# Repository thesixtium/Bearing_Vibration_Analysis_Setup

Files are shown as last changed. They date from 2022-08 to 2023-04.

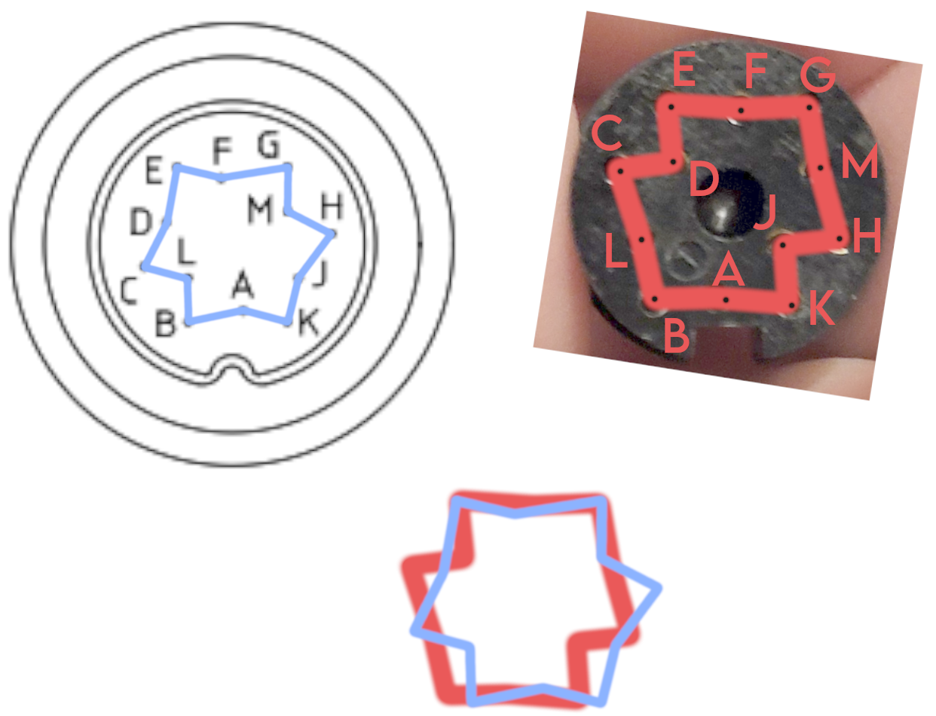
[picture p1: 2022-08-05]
Hole Alignment.png

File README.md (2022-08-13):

## Bearing Vibration Analysis Setup
I worked on the electrical and software design for this project. It is *extremely* loosely based on the setup shown in "A Novel Tribometer Designed
to Evaluate Geological Sliding
Contacts Lubricated by Drilling Muds" in the Journal of Testing and Evaluation, published by Philip Egberts, Nicholas Simin, Calvin Wong, Jan Czibor, Curtis Ewanchuk, and Simon Par.

The goal of this project is to research faults in bearings, and see if specific vibrations can be recorded to predict not only a fault in a bearing ahead of time but also what the fault is caused by.

The two main parts of this project was electrically connecting everything properly, and then coding everything to work. The main electrical parts are:
* NI myDAQ
* AC Motor
* Torque Sensor
* AC Motor PSU
* Torque Sensor PSU

The electrical was mostly just wiring connections between different parts, however, an opamp had to be wired and installed to allow a voltage range expansion on the controlling DAQ.

The software was all done in LabVIEW and was focused on getting the torque sensor to act in a feedback loop with the motor in order to control the motor's speed.

I made good progress on this project, but there was just not enough time to finish it during my summer term.

### Link to GitHub
You can find the project-specific GitHub here:
[thesixtium/Bearing_Vibration_Analysis_Setup](https://github.com/thesixtium/Bearing_Vibration_Analysis_Setup)

### What's Been Done
* The electrical schematics were made according to specifications by the head Ph.D. student. 
* Version 1 of the electrical setup was tested. It didn’t reach the full 42V range because of an oversight in the opamp chip (although rated to go to a full 42V, it only had a gain of 5V). Everything else worked through.
* Version 2 of the electrical was tested. Everything seemed to work, but because the opamp came in a smaller package than expected (TSSOP) and because the protoboard was being soldered by hand, this lead to a short that caused the board to fail.

### What Needs to Happen
* The protoboard that is the current circuit needs to be redone to fix the solder. Instead of ordering more parts and trying to do everything by hand, I would recommend making an actual PCB for it. The protoboard was only tried because it was faster and guaranteed to give me enough time for 2 attempts and was easy to resolder parts if needed. Redo circuit board, probably print an actual PCB
* Range scaling and calibration need to be added to the LabVIEW program to allow for easier control of the motor feedback loop. Currently, the numbers are not mapped to any understandable value and are pretty arbitrary outside of having a mix between a logarithmic and linear relationship with the motor's speed.
* The integration of the accelerometers and brake integration needs to be done, they weren't a priority at the start of this project for electrical so they were largely ignored.

### Documentation
All the needed documentation is on the project's GitHub, with “Bearing Information.pptx” being the most up-to-date and informative file on everything. There is also a bunch of supporting documentation.

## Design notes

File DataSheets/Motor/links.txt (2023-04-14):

http://wentec.com/unipower/calculators/power_torque.asp?print=true
https://www.usarollerchain.com/90-Volt-1-3-HP-DC-Electric-Motor-p/wpmdc13-18-90v-56cb.htm
https://worldwideelectric.com/product/wpmdc14-18-90v-56cb/

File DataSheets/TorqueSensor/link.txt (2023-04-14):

httpswww.kistler.comINTencpshaft-torque-sensors-basic-line-torque-transducers-measuring-ranges-1-to-1000-nm-4520aP0000241

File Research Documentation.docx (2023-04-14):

Research Documentation

# The Parts

## PCB

### PCB Schematics

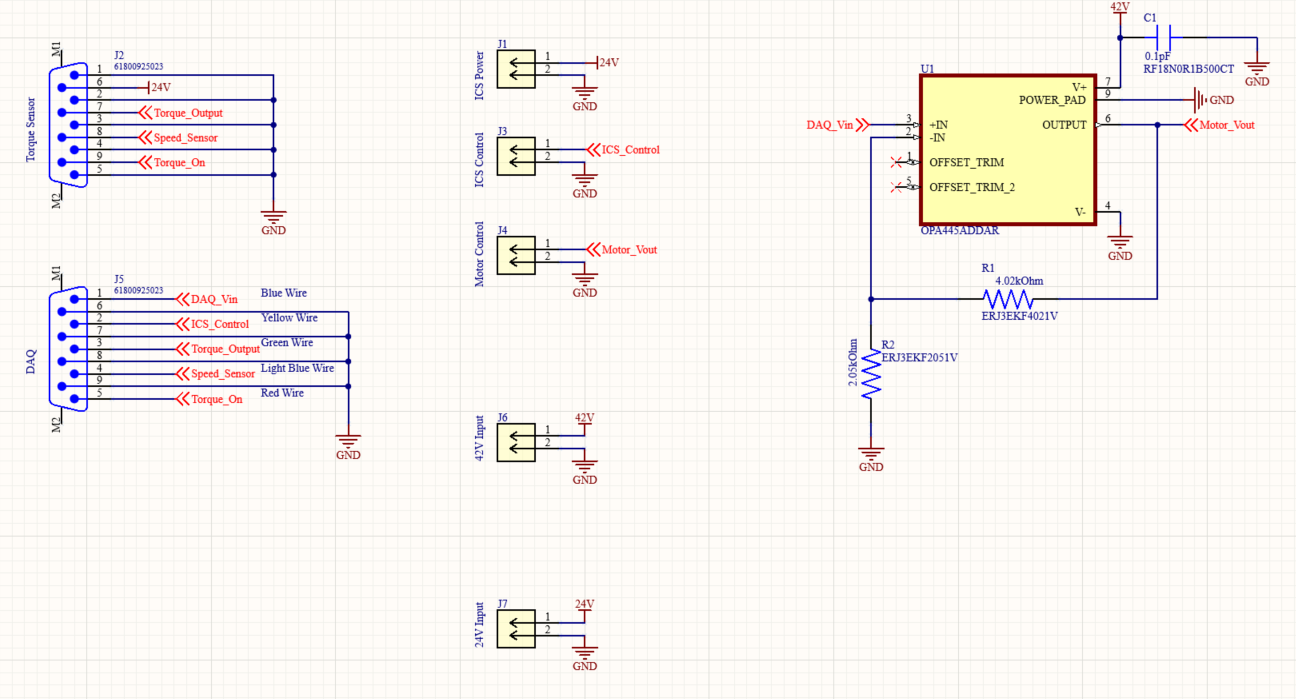
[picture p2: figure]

#### How to read the above schematic

All red and red-adjacent labels are “net labels”; all blue wires connected to the same net label are connected together. For example, everything connected to the “ICS_Control” label is connected together.

The two parts labeled “Torque Sensor” and “DAQ” are db 9 connectors, specifically the “61800925023” connector available on DigiKey at the following link: 61800925023 Würth Elektronik | Connectors, Interconnects | DigiKey (https://www.digikey.com/en/products/detail/w%C3%BCrth-elektronik/61800925023/10484653). They are serial connectors used to connect the torque sensor and the DAQ to other components.

The five yellow squares (each one has two arrows pointing to the left) are BNC connectors, similar in function to the db 9 connectors. They are all labeled to what they connect to, which (top to bottom) is the power for the ICS, the control signals for the ICS, the control signals for the motor, the input connector for the 42 volt supply, and the input connector for the 24 volt supply.

Finally, the circuit on the right is a whole bunch of components connected together to form an amplifier, to change the output from the DAQ from a range of [0v, 15v] to [0v, 42v]. The circuit is a negative feedback operational amplifier circuit. The big yellow box in the middle (labeled on top at U1, and on the bottom as OPA445ADDAR) is an operational amplifier, usually known as an op-amp, and functions to add gain to the voltage. It is configured in a negative feedback loop, which is when you connect the output of an op-amp to its inverting (-) input. It makes a dynamic system where the output signal is “fed back” to the input somehow so as to reach a point of equilibrium, which in this case is an amplification of about 3 times. The two resistors (R1 and R2, represented by zigzag lines) set what the gain of the amplifier will be. The equation for gain is 1+(R2/R1), thus the gain of this circuit is about 1+(4/2) = 3.

< - - - Documentation Stopped As Documentation Is No Longer Needed - - ->

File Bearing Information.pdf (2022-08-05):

# Bearing Testing Rig

## What Aleks has done

# Week 1

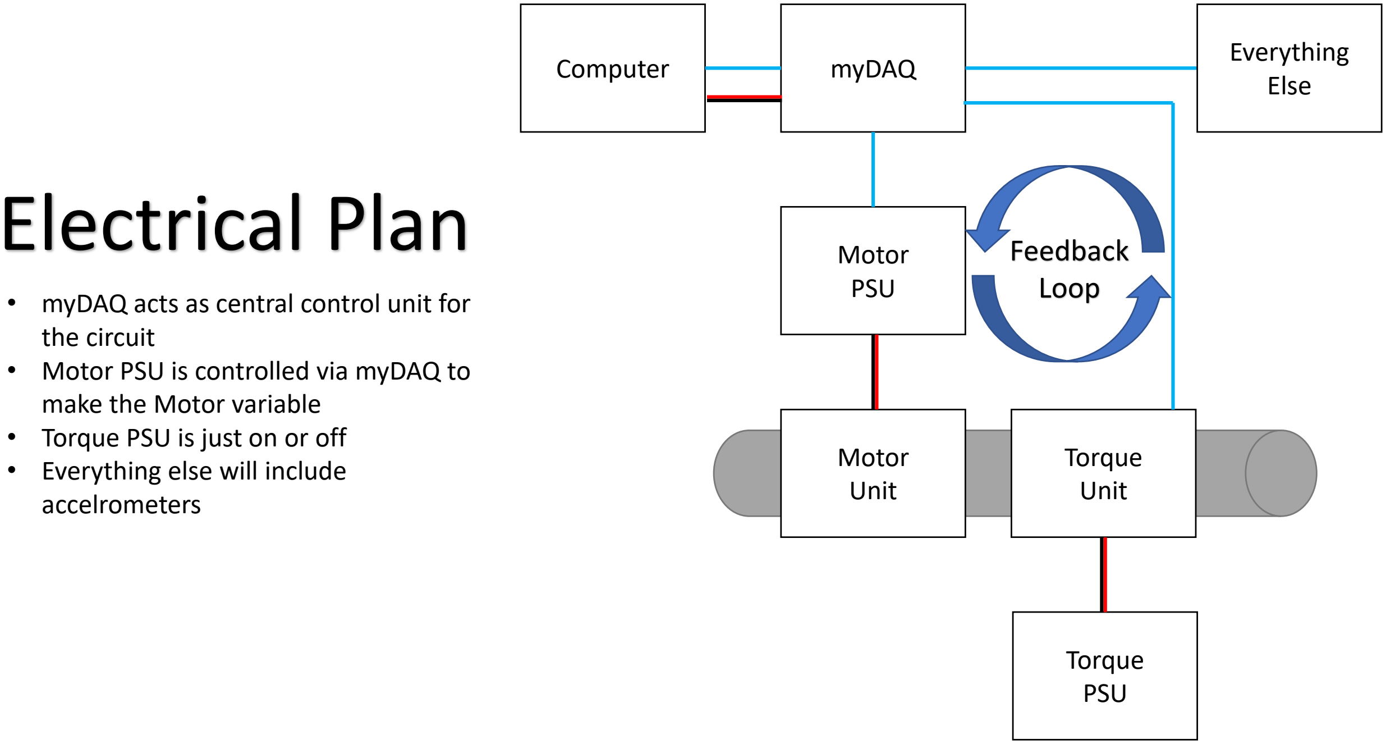
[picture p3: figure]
myDAQ; Motor PSU; Torque PSU; Computer; Torque Unit; Motor Unit; Everything Else; Feedback Loop; Electrical Plan; the circuit • Motor PSU is controlled via myDAQ to make the Motor variable • Torque PSU is just on or off • Everything else will include accelrometers

- myDAQ acts as central control unit for

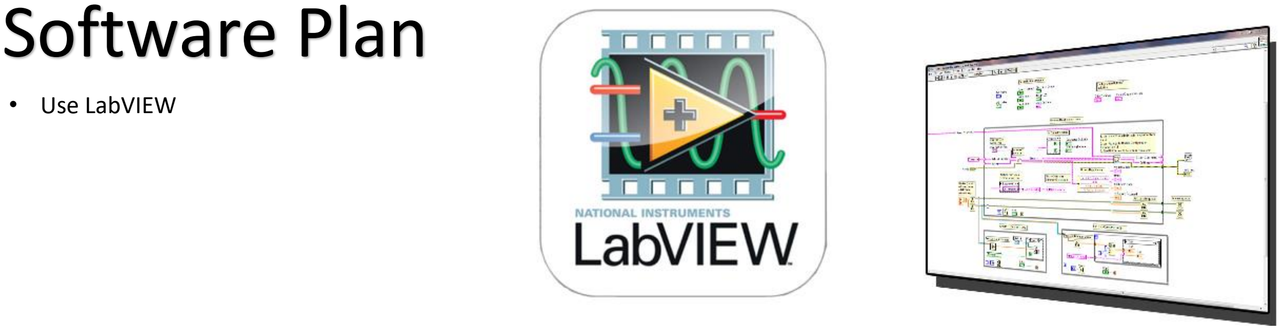
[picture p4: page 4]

# Software Plan

- Use LabVIEW

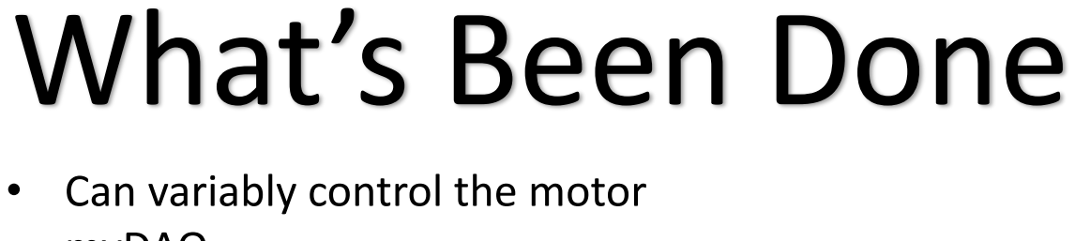
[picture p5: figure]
What’s Been Done; • Can variably control the motor

myDAQ
- Need the cable for the torque sensor to do the rest of it
- Need to know what “Everything Else” entails
- How do we want the data out?

# Week 2

# EM Brake: AHB-5 Air-Cooled Hysteresis Brake

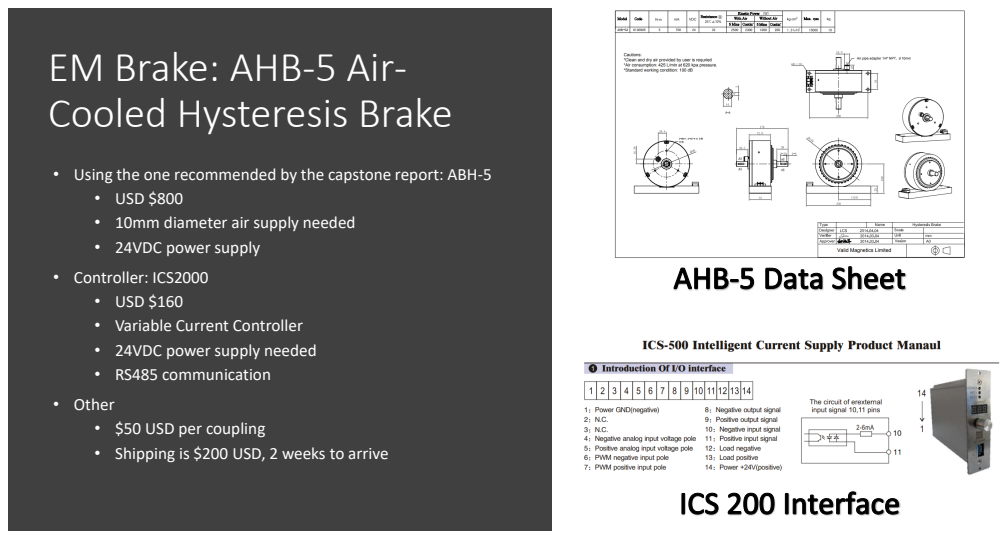
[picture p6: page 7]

• Using the one recommended by the capstone report: ABH-5
• USD $800
• 10mm diameter air supply needed
• 24VDC power supply
• Controller: ICS2000
• USD $160
• Variable Current Controller
• 24VDC power supply needed
• RS485 communication
• Other
• $50 USD per coupling
• Shipping is $200 USD, 2 weeks to arrive

# Accelerometers

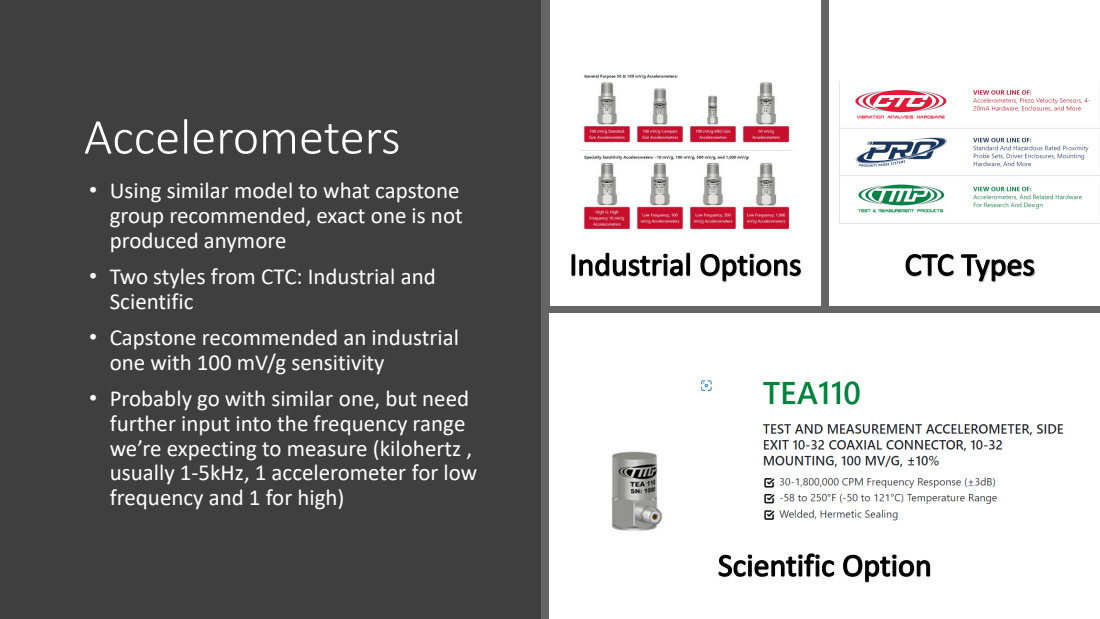
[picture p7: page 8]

• Using similar model to what capstone
group recommended, exact one is not
produced anymore
• Two styles from CTC: Industrial and
Scientific
• Capstone recommended an industrial
one with 100 mV/g sensitivity
• Probably go with similar one, but need
further input into the frequency range
we’re expecting to measure (kilohertz ,
usually 1-5kHz, 1 accelerometer for low
frequency and 1 for high)

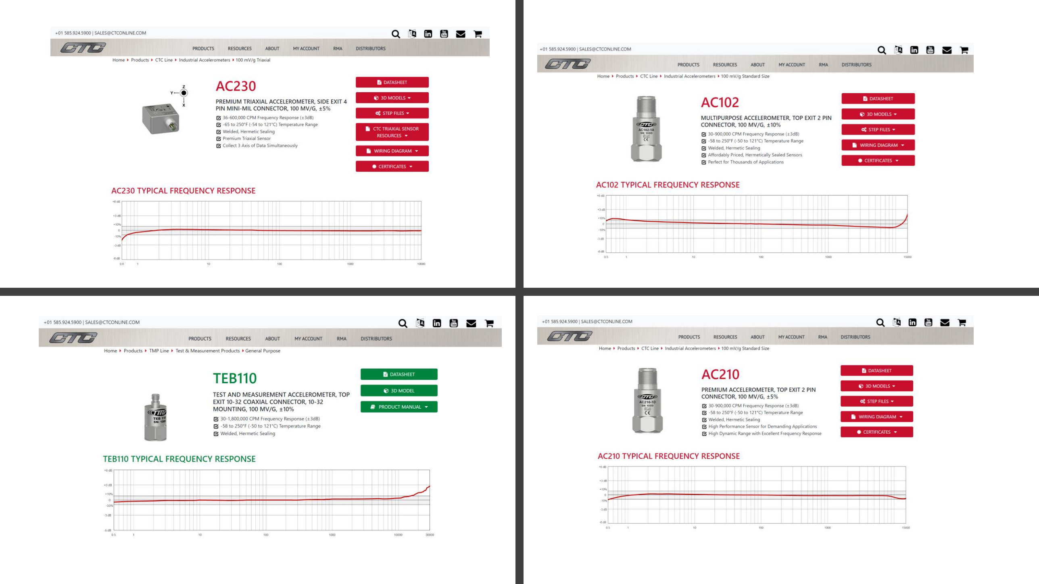
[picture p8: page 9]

# Pricing

| AC230 | AC102 | TEB110 | AC210
Frequency Low (Hz) | 0.8 | 2 | 0.5 | 0.6
Frequency High (Hz) | 10000 | 11200 | 10000 | 15000
Axis | 3 | 1 | 1 | 1
Sensitivity (mV/g) | 100 | 100 | 100 | 100
Error | 5% | 10% | 10% | 5%
Price (Low) | $ 1,276.22 $ 113.10 $ 262.35 $ 229.70
Price (High) | $ 1,496.22 $ 288.00 $ 262.35 $ 257.96
Total Price (Low) | $ 1,276.22 $ 339.30 $ 787.05 $ 689.10
Total Price (High) | $ 1,496.22 $ 864.00 $ 787.05 $ 773.88
- Recommend AC210 • Very high frequency

range
- Good sensitivity • Low error margin • Good price

# Week 3

# DAQ Amp

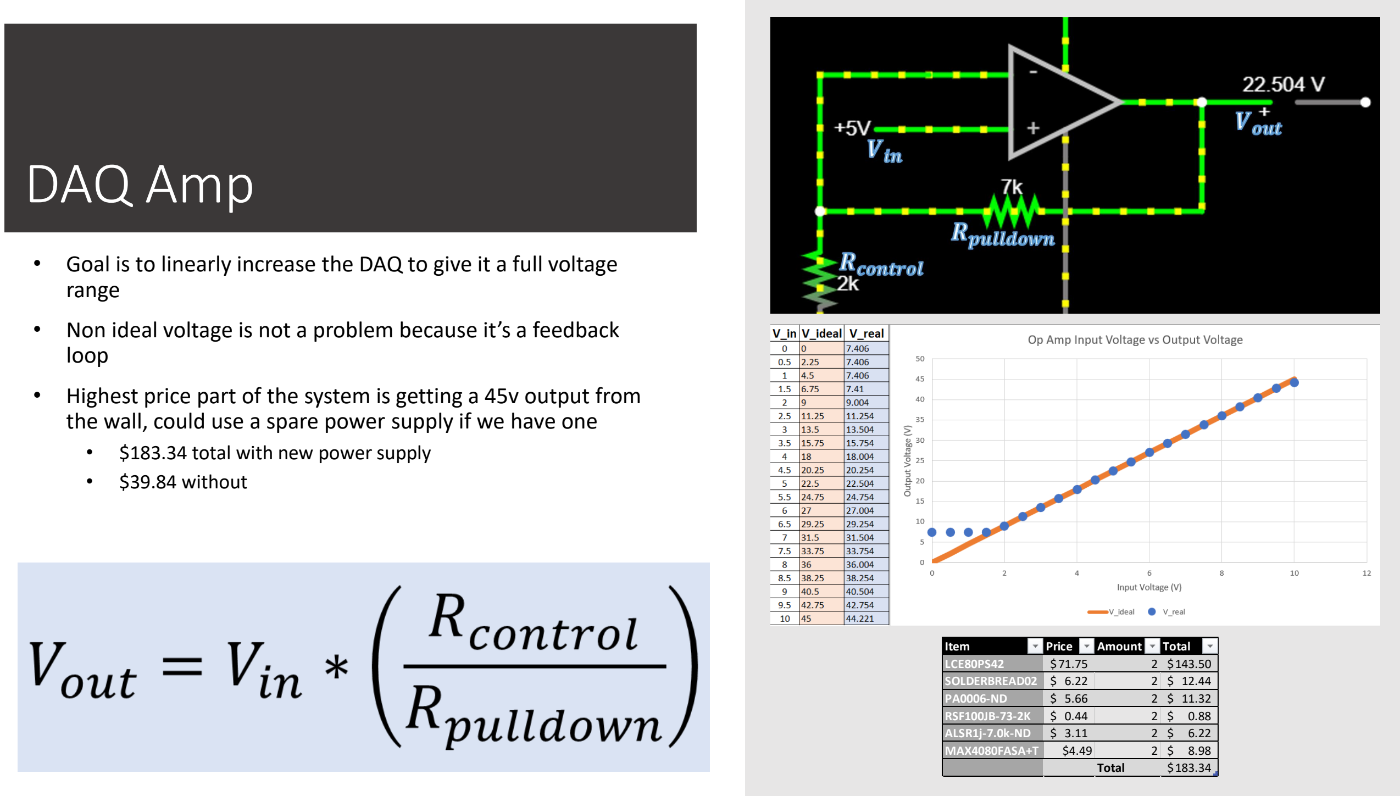
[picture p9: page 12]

- Goal is to linearly increase the DAQ to give it a full voltage range
- Non ideal voltage is not a problem because it’s a feedback loop
- Highest price part of the system is getting a 45v output from the wall, could use a spare power supply if we have one
- $183.34 total with new power supply
- $39.84 without
Item | Price | Amount | Total
LCE80PS42 | $71.75 | 2 $143.50
SOLDERBREAD02 $ 6.22 | 2 | $ 12.44
PA0006-ND | $ 5.66 | 2 $ 11.32
RSF100JB-73-2K | $ 0.44 | 2 | $ 0.88
ALSR1j-7.0k-ND | $ 3.11 | 2 $ 6.22
MAX4080FASA+T | $4.49 | 2 | $ 8.98
| | Total | $183.34

## The Load

From Iurii Storozhenko:
Two types of loads: Electromagnetic particle break and Generator.
EMP break
- Simplest : Easy to use, and easy to control
- Usually used in test rigs
- Torque can be controlled very accurately
- Ideal for tension control, load simulation, cycling/indexing, and soft starts and stops
- If goal is to use vibration from the drivetrain and not current signals from the generator, this is ideal
Generator
- Main limitation is the control system
- Not sure of range where we can control the load with permanent magnet generator
- Control system of a doubly-fed induction generator is one of the most complicated
- Speed range in a wind turbine in which the generator can be operated is about +-30% of the generator's nominal speed.
- Also need to make the gearbox gear ratio appropriate to the generator

# TL;DR: EMP Break is easy to use and is used in a lot of test rigs. Generator is confusing and I don’t see any pros to it*

*this is very outside of my area of expertise, so I may be missing the reason we’re thinking of a generator at all

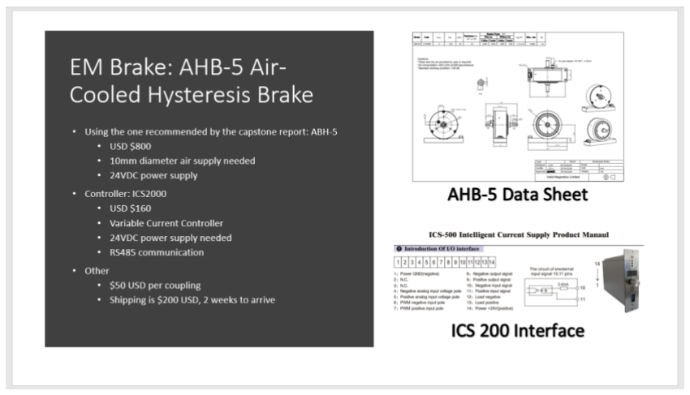
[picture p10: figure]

# Finding A Generator

Generator Specs:
- p = Rated Power in Watts
- z = Generator Efficiency in Percent

Variables:
- T = Torque in (hopefully) Newton Meters
- p’ = Rater Power in Kg-m/s
- y = Shaft rotations per second

T =

p

′ Kg m
sec
2 π ∗ y

rotations
sec

∗ z%

p

′

Kg m
sec

=

T ∗ 2 π ∗ y

rotations
sec
z%

p in
Watts

p’ in
Kg-m/sec

Need help finding y, T, and z.
Use power in watts to find generator

# Accelerometer

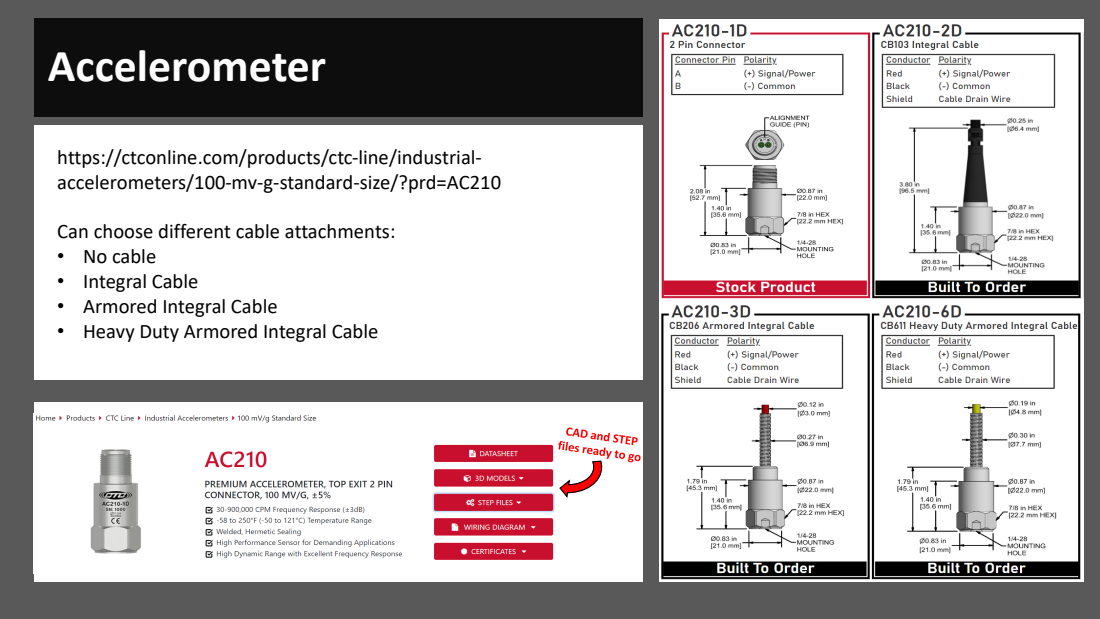
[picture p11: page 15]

https://ctconline.com/products/ctc-line/industrial-
accelerometers/100-mv-g-standard-size/?prd=AC210

Can choose different cable attachments:
• No cable
• Integral Cable
• Armored Integral Cable
• Heavy Duty Armored Integral Cable

# Week 4

# Pricing and Lead Time

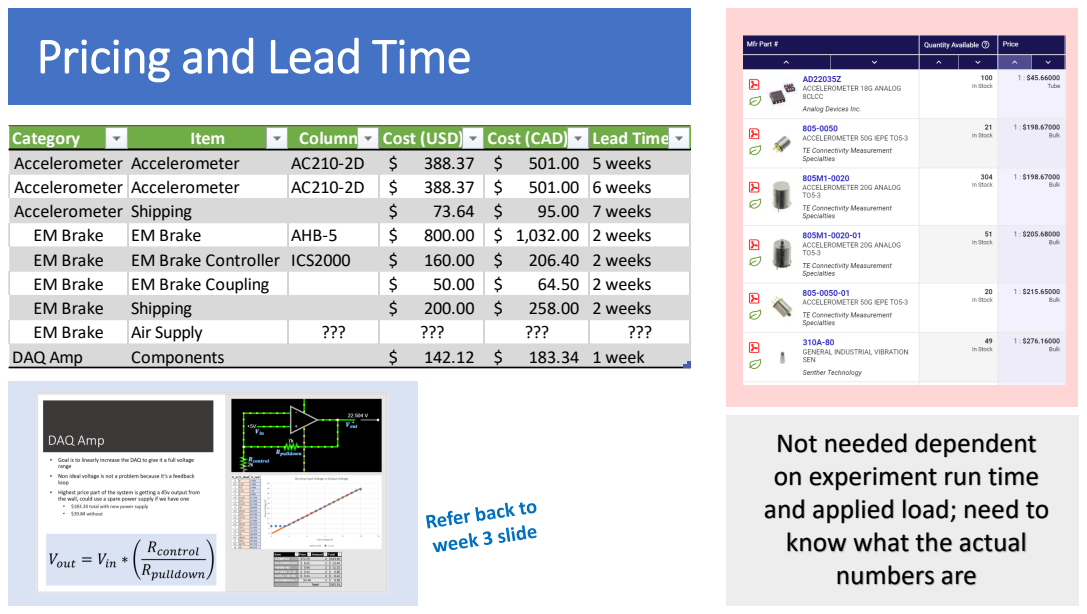
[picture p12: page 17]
Category; Item; Column1 Cost (USD); Cost (CAD); Lead Time; Accelerometer Accelerometer; 501.00 5 weeks; Accelerometer; 6 weeks; Accelerometer Shipping; 95.00 7 weeks; EM Brake; AHB-5; 2 weeks; EM Brake Controller ICS2000; 206.40 2 weeks; EM Brake Coupling; Shipping; 258.00 2 weeks; Air Supply; DAQ Amp; Components; 183.34 1 week

Not needed dependent
on experiment run time
and applied load; need to
know what the actual
numbers are

# Pricing and Lead Time

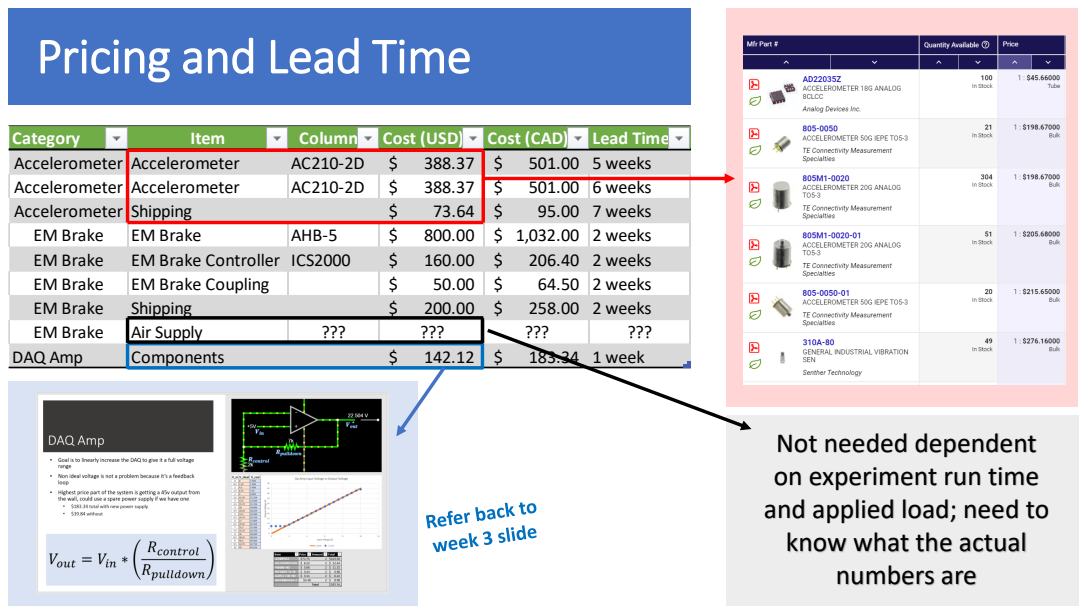
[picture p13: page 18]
Category; Item; Column1 Cost (USD); Cost (CAD); Lead Time; Accelerometer; 501.00 5 weeks; 6 weeks; Shipping; 95.00 7 weeks; EM Brake; AHB-5; 2 weeks; EM Brake Controller ICS2000; 206.40 2 weeks; EM Brake Coupling; 258.00 2 weeks; Air Supply; DAQ Amp; Components; 183.34 1 week

Not needed dependent
on experiment run time
and applied load; need to
know what the actual
numbers are

# Week 5

# Voltage Divider

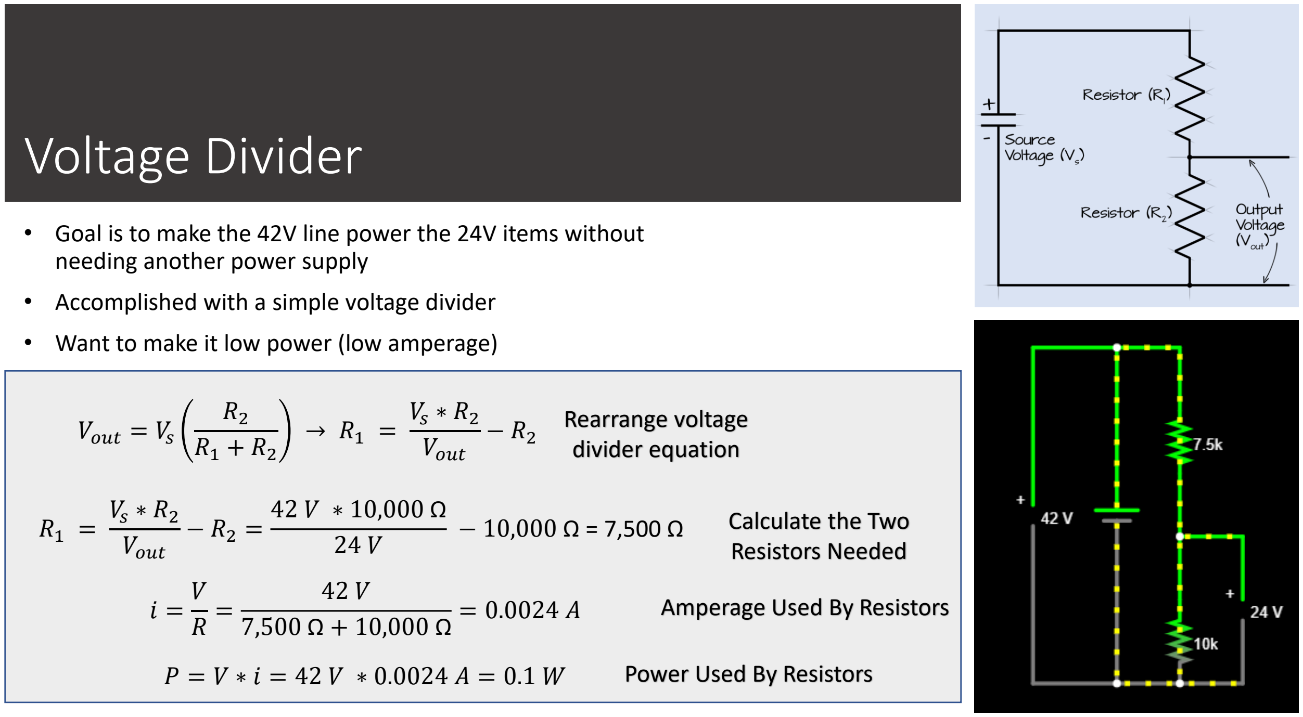
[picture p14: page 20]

i =

V
R

=

42 V
7,500 Ω + 10,000 Ω

= 0.0024 A

Vout = Vs

R2
R1 + R2

→ R1 =

Vs ∗ R2

Vout

− R2

R1 =

Vs ∗ R2

Vout

− R2 =

42 V ∗ 10,000 Ω
24 V

− 10,000 Ω = 7,500 Ω

- Goal is to make the 42V line power the 24V items without needing another power supply
- Accomplished with a simple voltage divider
- Want to make it low power (low amperage)

P = V ∗ i = 42 V ∗ 0.0024 A = 0.1 W

Calculate the Two
Resistors Needed

Amperage Used By Resistors

Power Used By Resistors

Rearrange voltage
divider equation

# Full Circuit

Notes:

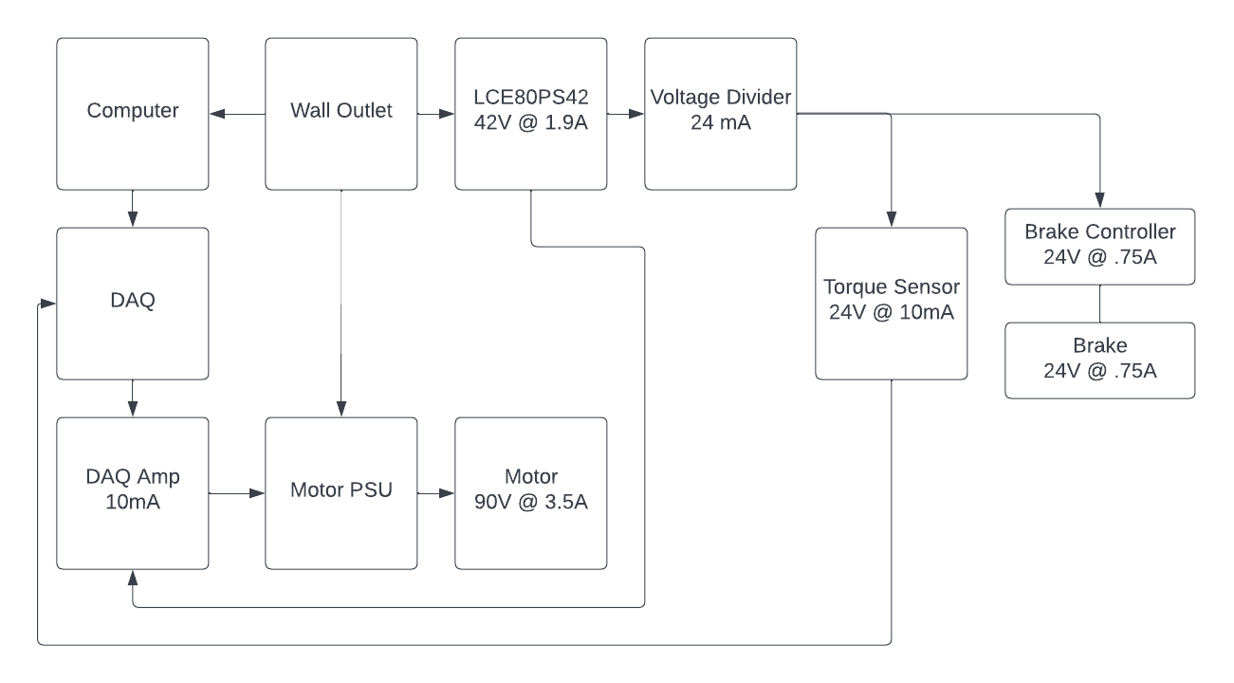
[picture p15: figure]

- All wiring will be done on a

protoboard

- Accelerometers will be on a

separate circuit (with a separate

DAQ) due to restrictions of

myDAQ

- Should see no issues going

forward

Air Consumption = 425 L
min @ 620 kpa = 112.3

gal
min @ 90 psi

Q =

πD

4∆P
128μ∆x

,Q

′ = Q ∗ c, ∴ Q

′ =

πD

4∆P
128μ∆x

∗ c

Known Variables:
∆P = pressure = 90 psi = 620,528.4 Pa
μ = viscosity = 18.6 μPa ∗ s = 0.0000186 Pa ∗ s

c = Conversion Rate = 15.8503

ൗ

gal
min
lൗs

Assumed Variables
D = Pipe Diameter = 0.004 m

Unknown Variables
∆x = Pipe Lengtℎ = m

Q = Flow Rate =

l
s
Q

′ = Flow Rate =

gal
min

Q

′ =

πD

4∆P
128μ∆x

∗ c =

π 0.004 m 4
∗ 620528.4 Pa
128 ∗ 0.0000186 Pa ∗ s ∗ ∆x

∗ 15.8503

ൗ

gal
min
lൗs

∆x =

πD

4∆P
128μQ′ ∗ c =

π 0.004 m 4
∗ 620528.4 Pa

128 ∗ 0.0000186 Pa ∗ s ∗ 112.3

gal
min

∗ 15.8503

ൗ

gal
min
lൗs

∆x = 0.03 m

Assuming pipe is laminar, can use the Poiseuille Equation to calculate the flow rate:

Air Brake Consumption

# Week 6

# Cable Building

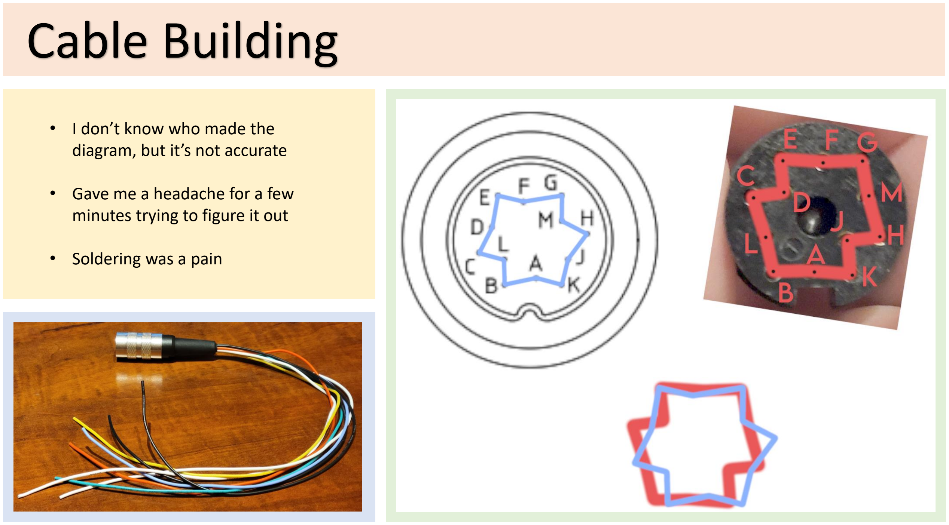
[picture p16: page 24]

- I don’t know who made the diagram, but it’s not accurate
- Gave me a headache for a few minutes trying to figure it out
- Soldering was a pain

# Wiring

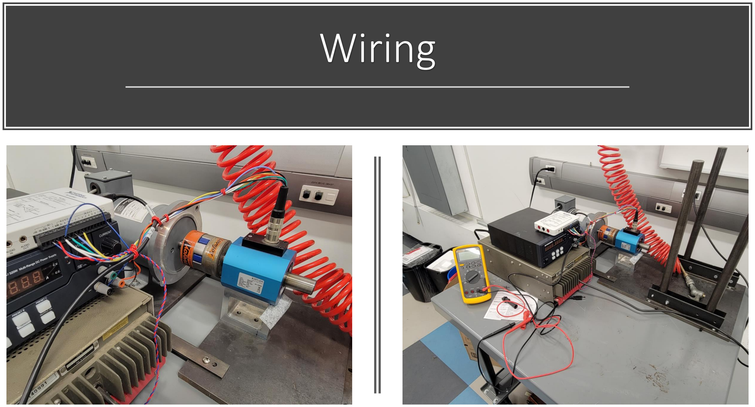
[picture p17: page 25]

# Air Supply

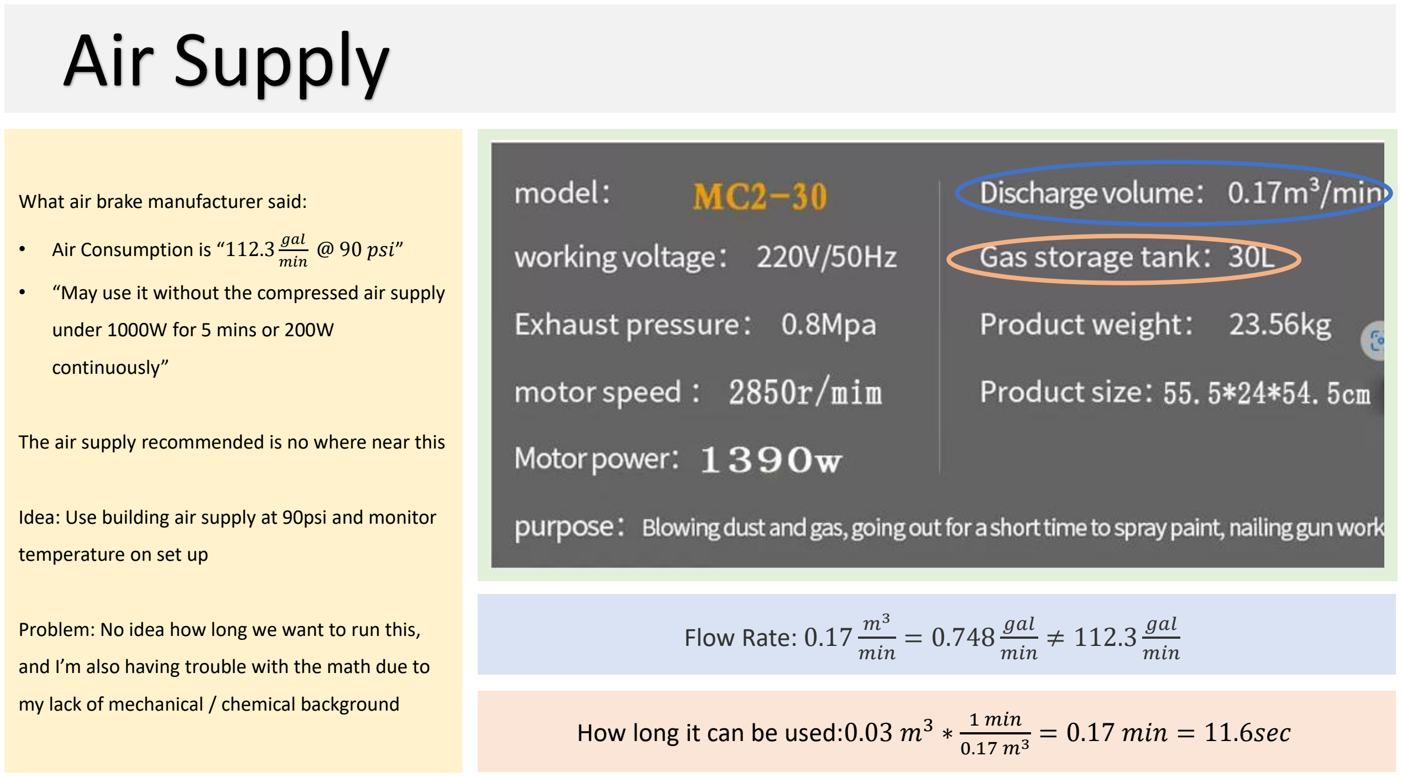
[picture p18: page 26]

What air brake manufacturer said:

- Air Consumption is “112.3

gal
min @ 90 psi”
- “May use it without the compressed air supply

under 1000W for 5 mins or 200W

continuously”

The air supply recommended is no where near this

Idea: Use building air supply at 90psi and monitor

temperature on set up

Problem: No idea how long we want to run this,

and I’m also having trouble with the math due to

my lack of mechanical / chemical background

Flow Rate: 0.17 m³
min

= 0.748 gal
min ≠ 112.3

gal
min

How long it can be used:0.03 m³ ∗

1 min
0.17 m³

= 0.17 min = 11.6sec

# Week 7

# Draft One of the Software is Done

# Draft One of

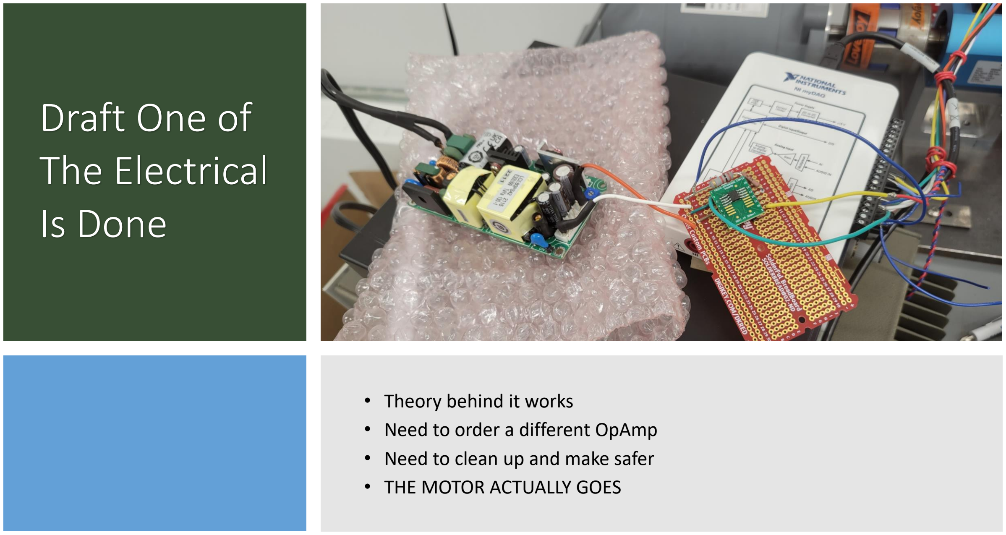
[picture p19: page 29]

# The Electrical Is Done

- Theory behind it works
- Need to order a different OpAmp
- Need to clean up and make safer
- THE MOTOR ACTUALLY GOES

# Powering The Brake

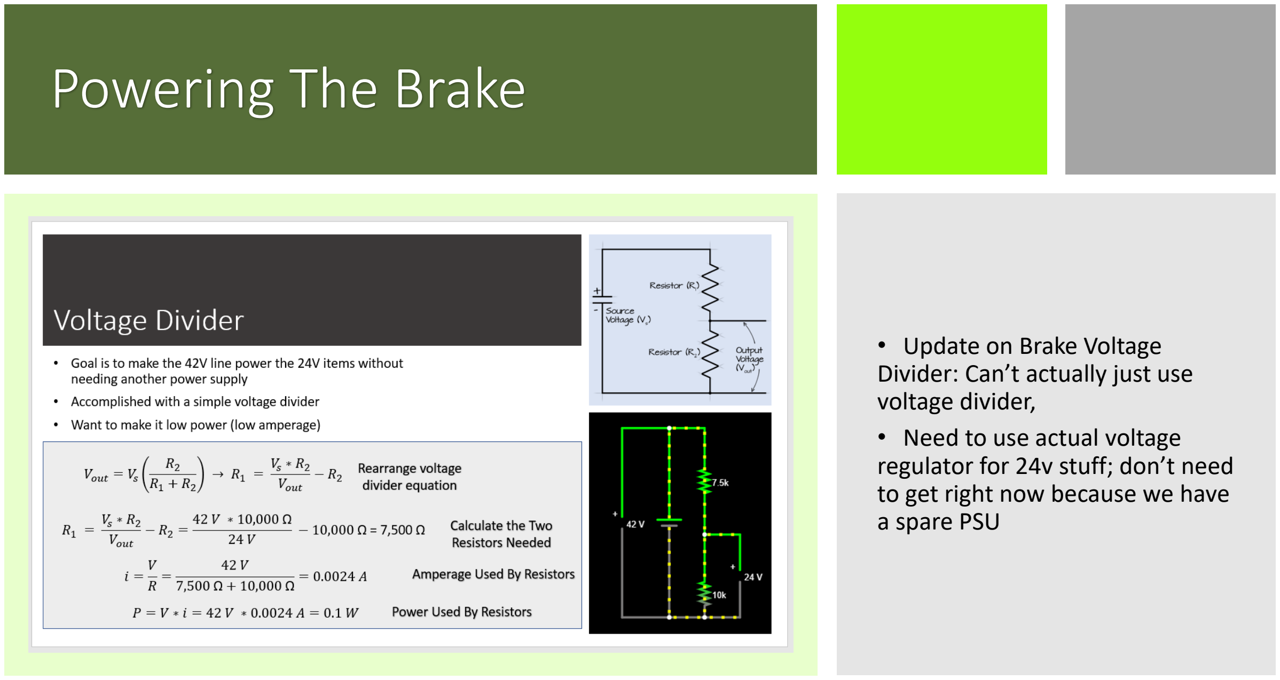
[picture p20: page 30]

- Update on Brake Voltage
Divider: Can’t actually just use voltage divider,
- Need to use actual voltage regulator for 24v stuff; don’t need to get right now because we have a spare PSU

# Electrical Wiring Box

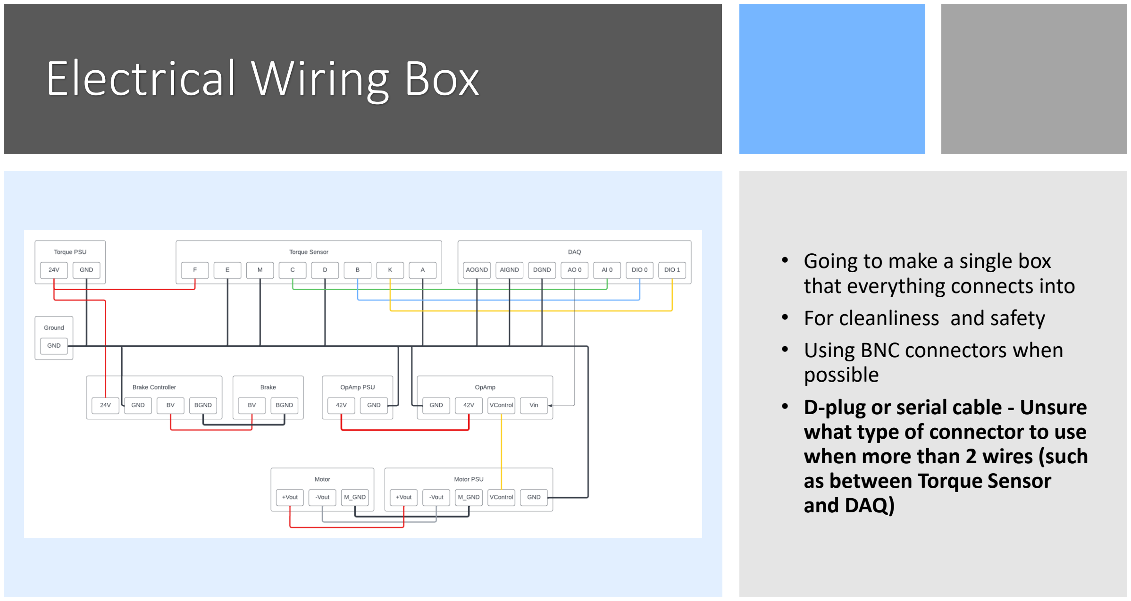
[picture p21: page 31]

- Going to make a single box that everything connects into
- For cleanliness and safety
- Using BNC connectors when possible
- D-plug or serial cable - Unsure what type of connector to use when more than 2 wires (such as between Torque Sensor
and DAQ)

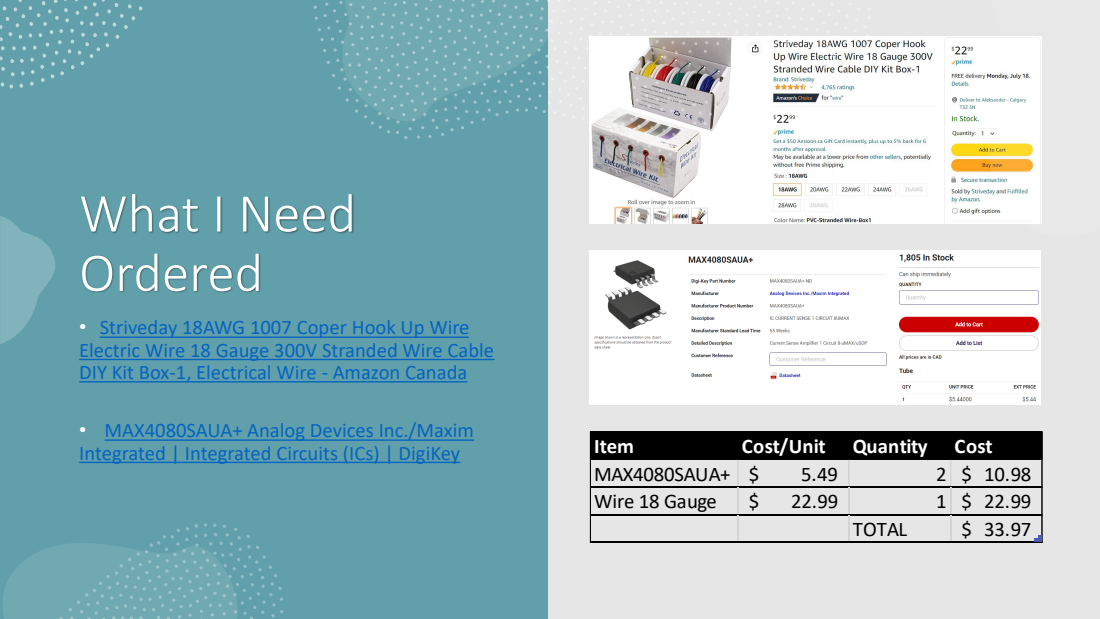
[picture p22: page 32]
What I Need Ordered; Item; Cost/Unit; Quantity; Cost

• Striveday 18AWG 1007 Coper Hook Up Wire
Electric Wire 18 Gauge 300V Stranded Wire Cable
DIY Kit Box-1, Electrical Wire - Amazon Canada (https://www.amazon.ca/StrivedayTM-18AWG-Coper-Electric-stranded/dp/B01LH1FQJ0)

• MAX4080SAUA+ Analog Devices Inc./Maxim
Integrated | Integrated Circuits (ICs) | DigiKey (https://www.digikey.ca/en/products/detail/analog-devices-inc-maxim-integrated/MAX4080SAUA/1702357)

MAX4080SAUA+ | $ 5.49 | 2 | $ 10.98
Wire 18 Gauge | $ 22.99 | 1 | $ 22.99

TOTAL | $ 33.97

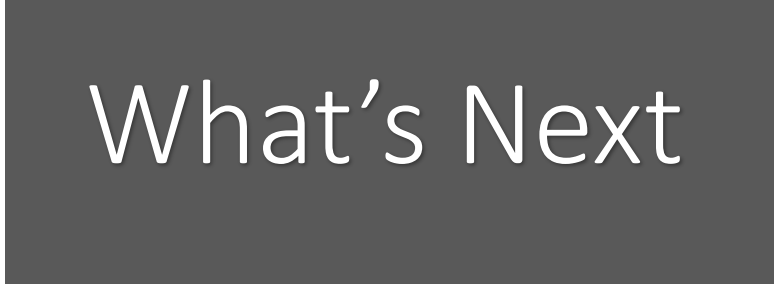
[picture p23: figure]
What’s Next

## - Order parts - Figure out connections needed for a wire box - Order all parts for wire box - Make wire box - 3D Print Casing for converter, solder board, and wire box - Resolder torque sensor wire and opamp boards to be nicer - Assemble - More software things

# Week 8

# Plug Layout

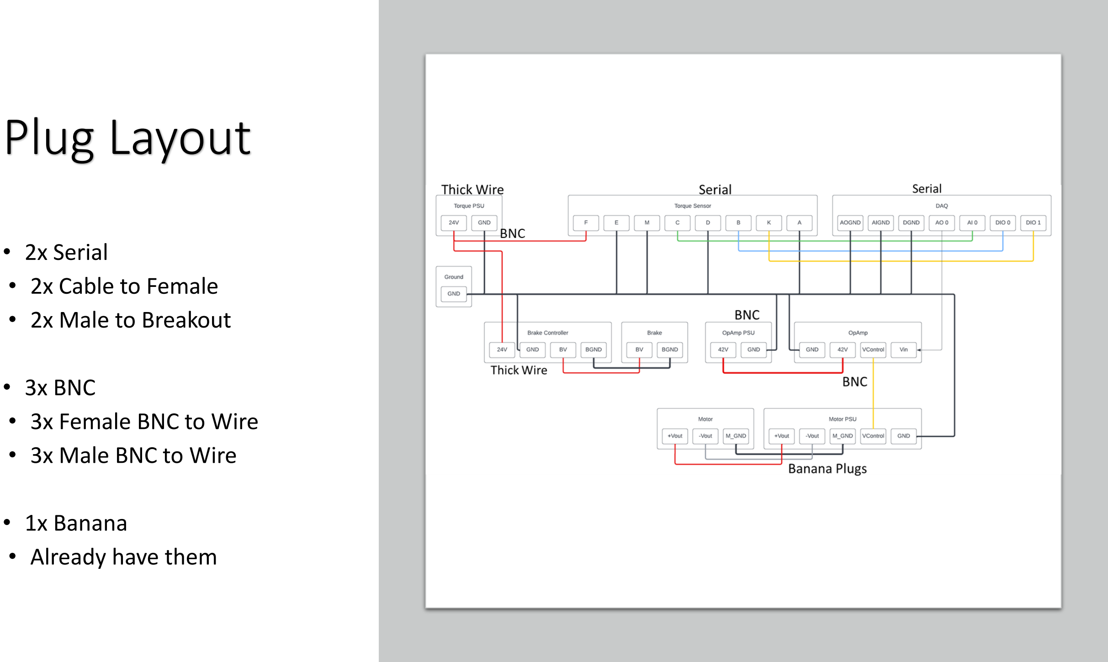
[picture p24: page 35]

- 2x Serial
- 2x Cable to Female
- 2x Male to Breakout
- 3x BNC
- 3x Female BNC to Wire
- 3x Male BNC to Wire
- 1x Banana
- Already have them

# Resoldering Cable To Be Longer And Serial

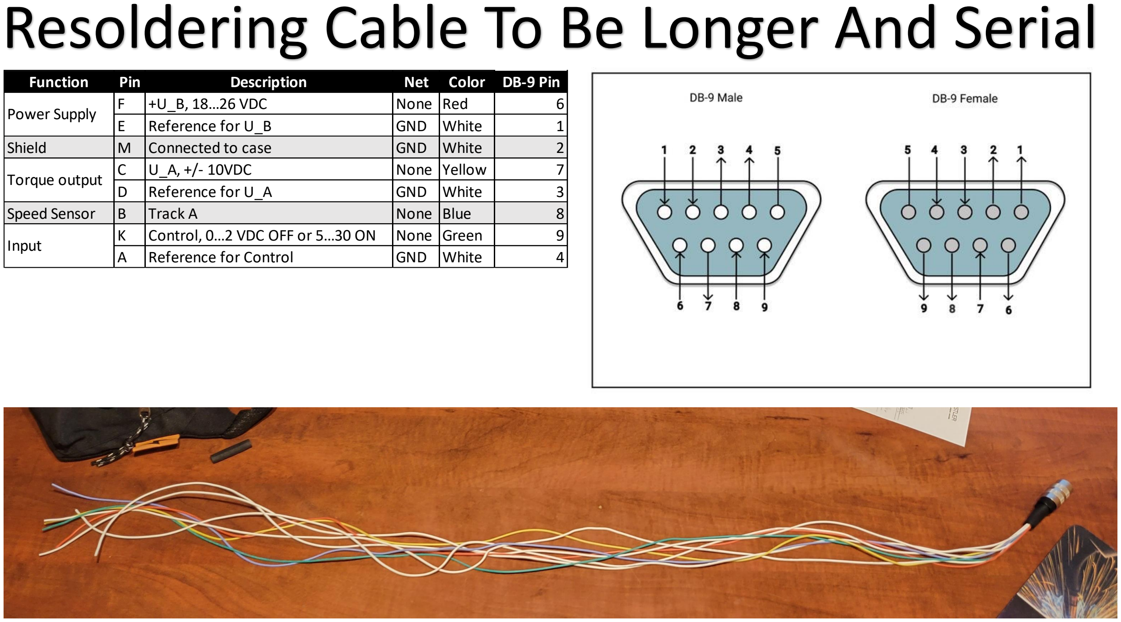
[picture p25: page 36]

Function | Pin | Description | Net | Color | DB-9 Pin
Power Supply | F | +U_B, 18…26 VDC | None | Red | 6
| E | Reference for U_B | GND | White | 1
Shield | M | Connected to case | GND | White | 2
Torque output | C | U_A, +/- 10VDC | None | Yellow | 7
| D | Reference for U_A | GND | White | 3
Speed Sensor | B | Track A | None | Blue | 8
Input | K | Control, 0…2 VDC OFF or 5…30 ON | None | Green | 9
| A | Reference for Control | GND | White | 4

# DAQ Is Also Going To Be Serial


DAQ Pin | DB-9 Pin
AOGND | 1
AIGND | 3
DGND | 5
AO 0 | 6
AI 0 | 7
DIO 0 | 8
DIO 1 | 9

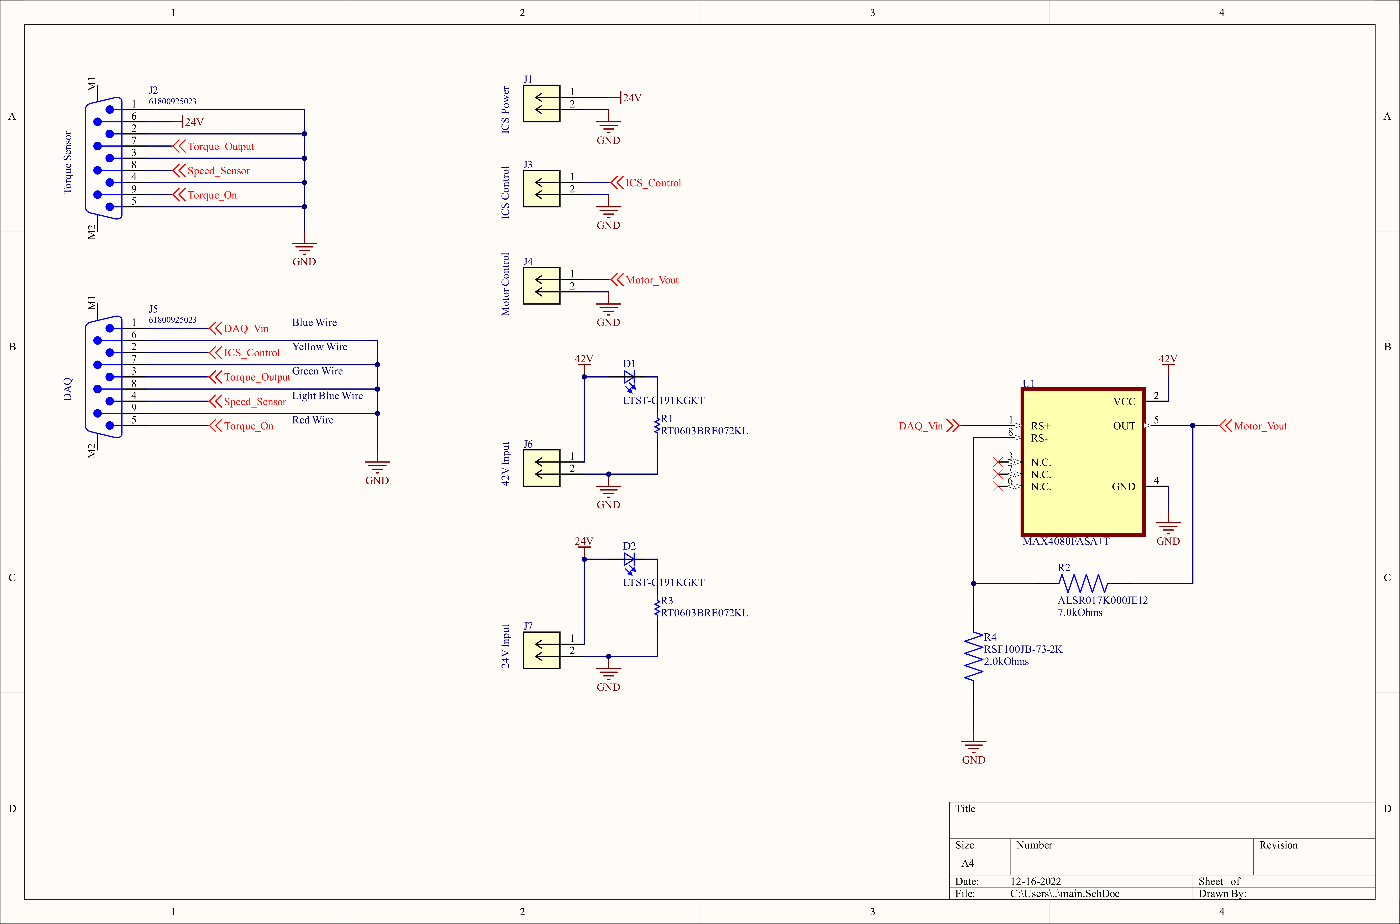
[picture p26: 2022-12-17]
RedditPost/Schematic.png

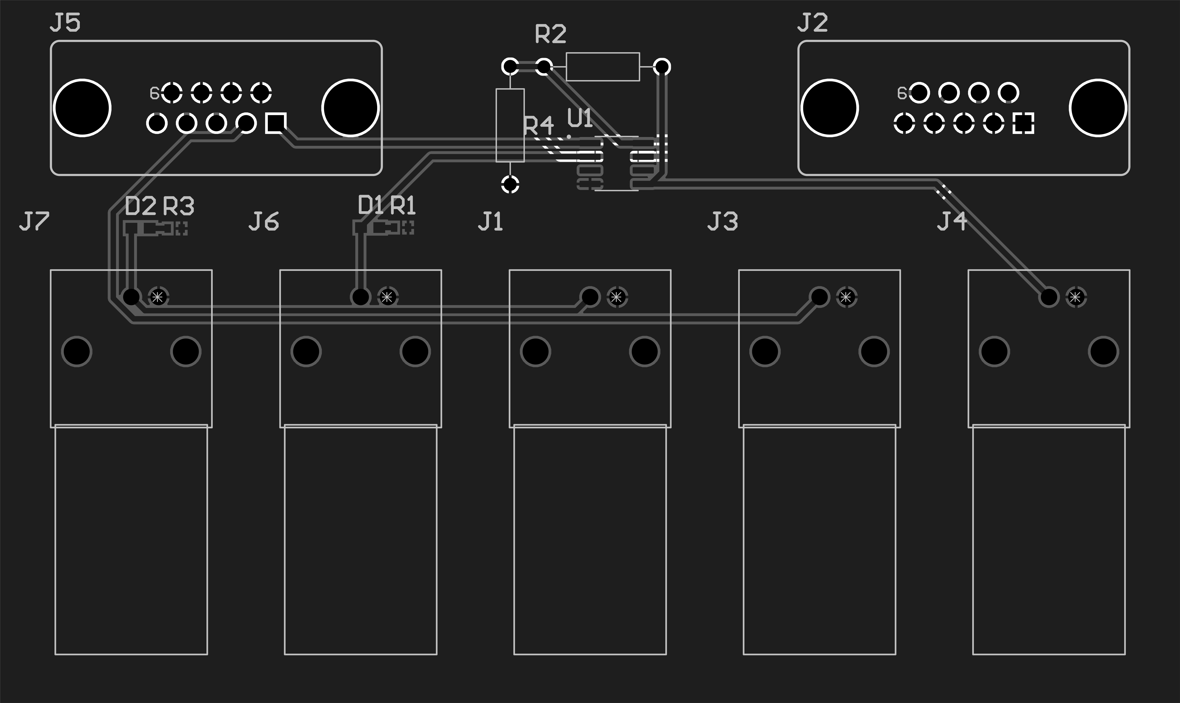
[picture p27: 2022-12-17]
RedditPost/Routing.png

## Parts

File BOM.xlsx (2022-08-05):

Part | Part # | Vendor | Status | Price/Part | Quantity | Price | Desc | Link
Torque Sensor Cable |  | Kislter | Pain | $28.92 | 2 | $57.84 | Cable to read from the torque sensor
EM Brake | AHB-5 | Valid Magnetics | Haven't Ordered |  | 1 | $0.00 | Apply load to the setup | Air-Cooled Hysteresis Brakes (validmagnetics.com) (https://www.validmagnetics.com/component/jshopping/air-cooled-hysteresis-brakes.html)
Accelerometers | AC196 |  | Haven't Ordered |  | 2 | $0.00 | Measure vibrations in the setup | AC196 Datasheet (ctconline.com) (https://ctconline.com/datasheet?type=Sensor&prd=AC196)
Motor Controller | DC-51 | Amazon | Haven't Ordered | $49.36 | 2 | $98.72 | Control the Motor | AC 110V Input DC 24V-90V Output Motor Speed Controller Switch Electric Speed Regulator for Permanent Magnet DC Motor 400W DC-51 : Amazon.ca: Tools & Home Improvement (https://www.amazon.ca/24V-90V-Controller-Electric-Regulator-Permanent/dp/B076KPP92X)

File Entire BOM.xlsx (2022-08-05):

Category | Item | Column1 | Cost (USD) | Cost (CAD) | Lead Time
Accelerometer | Accelerometer | AC210-2D | $388.37 | $501.00 | 5 weeks
Accelerometer | Accelerometer | AC210-2D | $388.37 | $501.00 | 6 weeks
Accelerometer | Shipping |  | $73.64 | $95.00 | 7 weeks
EM Brake | EM Brake | AHB-5 | $800.00 | $1032.00 | 2 weeks
EM Brake | EM Brake Controller | ICS2000 | $160.00 | $206.40 | 2 weeks
EM Brake | EM Brake Coupling |  | $50.00 | $64.50 | 2 weeks
EM Brake | Shipping |  | $200.00 | $258.00 | 2 weeks
EM Brake | Air Supply | ??? | ??? | ??? | ???
DAQ Amp | Components |  | $142.12 | $183.34 | 1 week

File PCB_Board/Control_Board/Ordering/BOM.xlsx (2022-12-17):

Comment | Designator | Footprint | JLCPCB Part #（optional）
RF18N0R1B500CT | C1 | 0603 | C304680
https://www.digikey.ca/en/products/detail/molex/0731375003/1465136 | J1, J3, J4, J6, J7 | CONN_73137-5003_MOL
61800925023 | J2, J5 | 61800925023
ERJ3EKF4021V | R1 | 0603 | C242164
ERJ3EKF2051V | R2 | 0603 | C403060
OPA445ADDAR | U1 | VREG_LM5017MR/NOPB | C1348607

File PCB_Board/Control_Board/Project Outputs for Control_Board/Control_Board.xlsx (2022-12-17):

Comment | Designator | Footprint
RF18N0R1B500CT | C1 | 0603
https://www.digikey.ca/en/products/detail/molex/0731375003/1465136 | J1, J3, J4, J6, J7 | CONN_73137-5003_MOL
61800925023 | J2, J5 | 61800925023
ERJ3EKF4021V | R1 | 0603
ERJ3EKF2051V | R2 | 0603
OPA445ADDAR | U1 | VREG_LM5017MR/NOPB

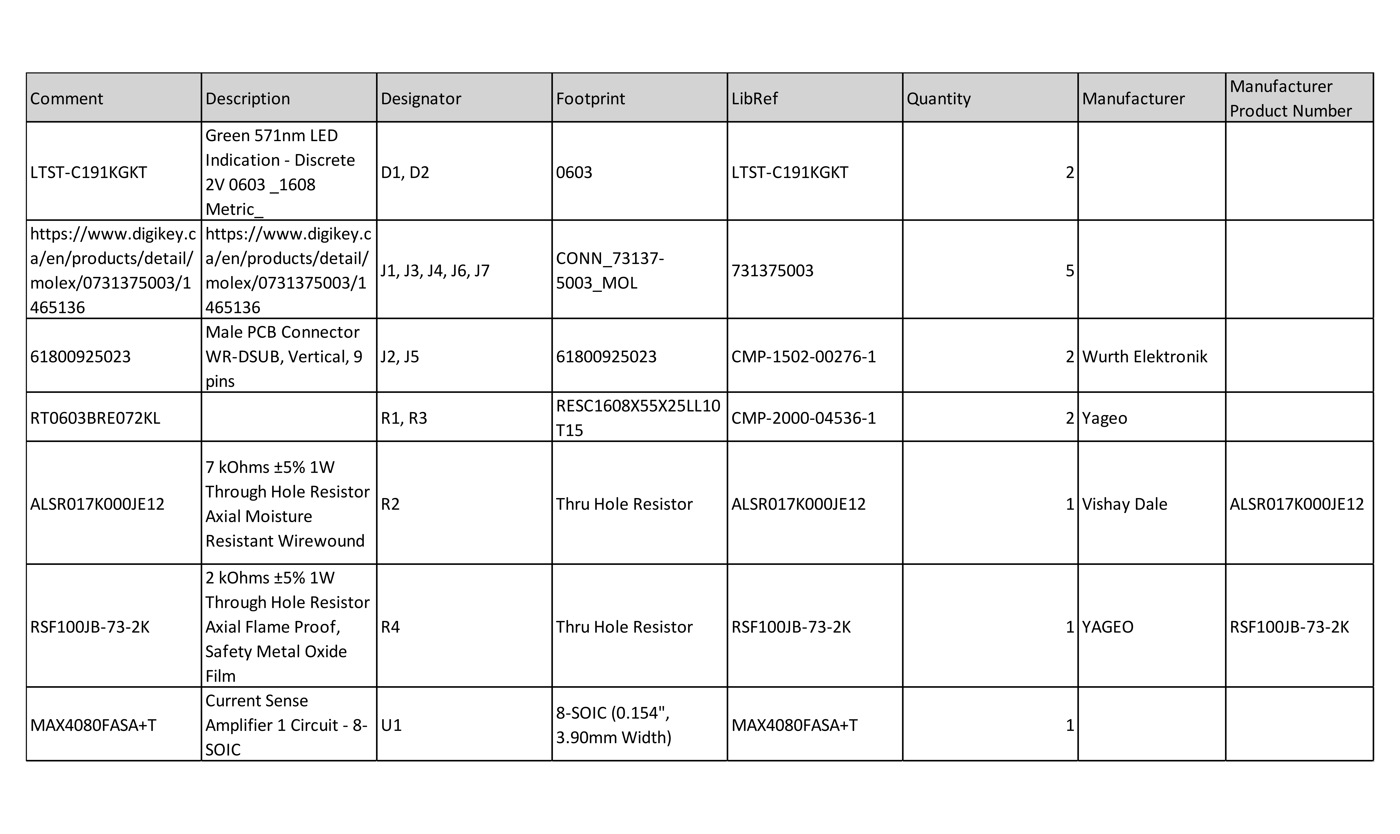
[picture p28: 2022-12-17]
RedditPost/BOM.png

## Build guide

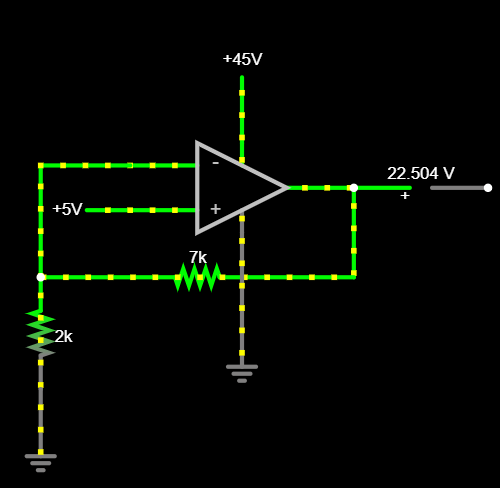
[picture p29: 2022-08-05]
OpAmpSetup.PNG

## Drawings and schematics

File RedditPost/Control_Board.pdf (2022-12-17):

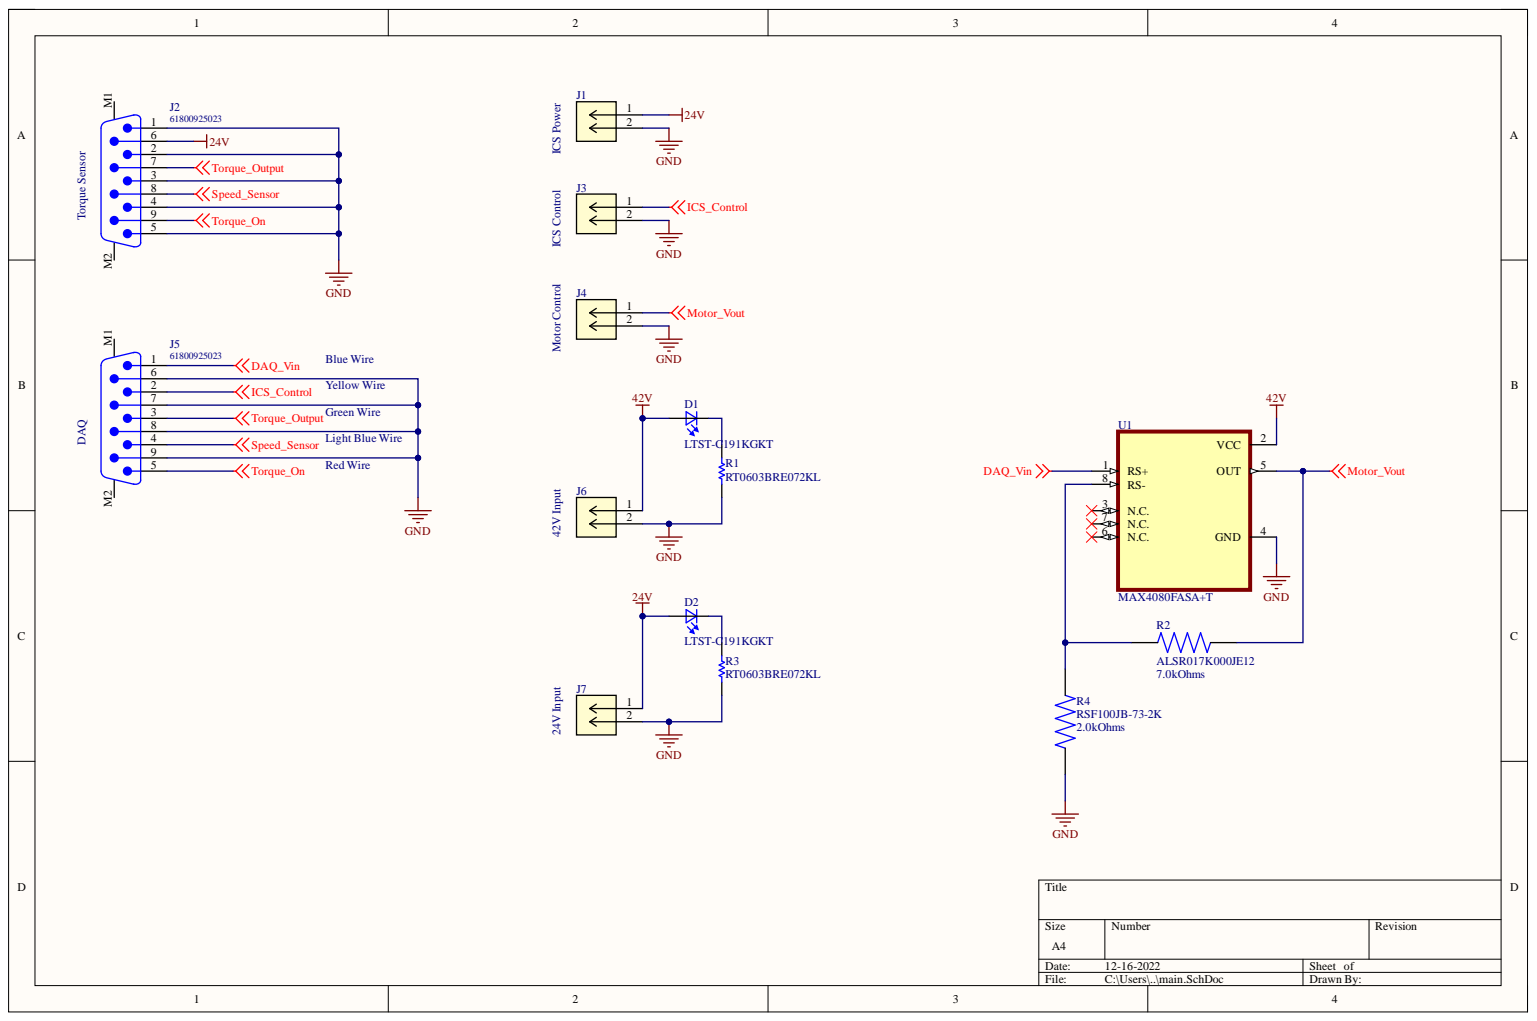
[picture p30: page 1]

ICS Control Motor Control 42V Input 24V Input

543219876 | Yel l o w W i re ICS_Co n t ro l

Green W ire Torq ue_ O u tp u t

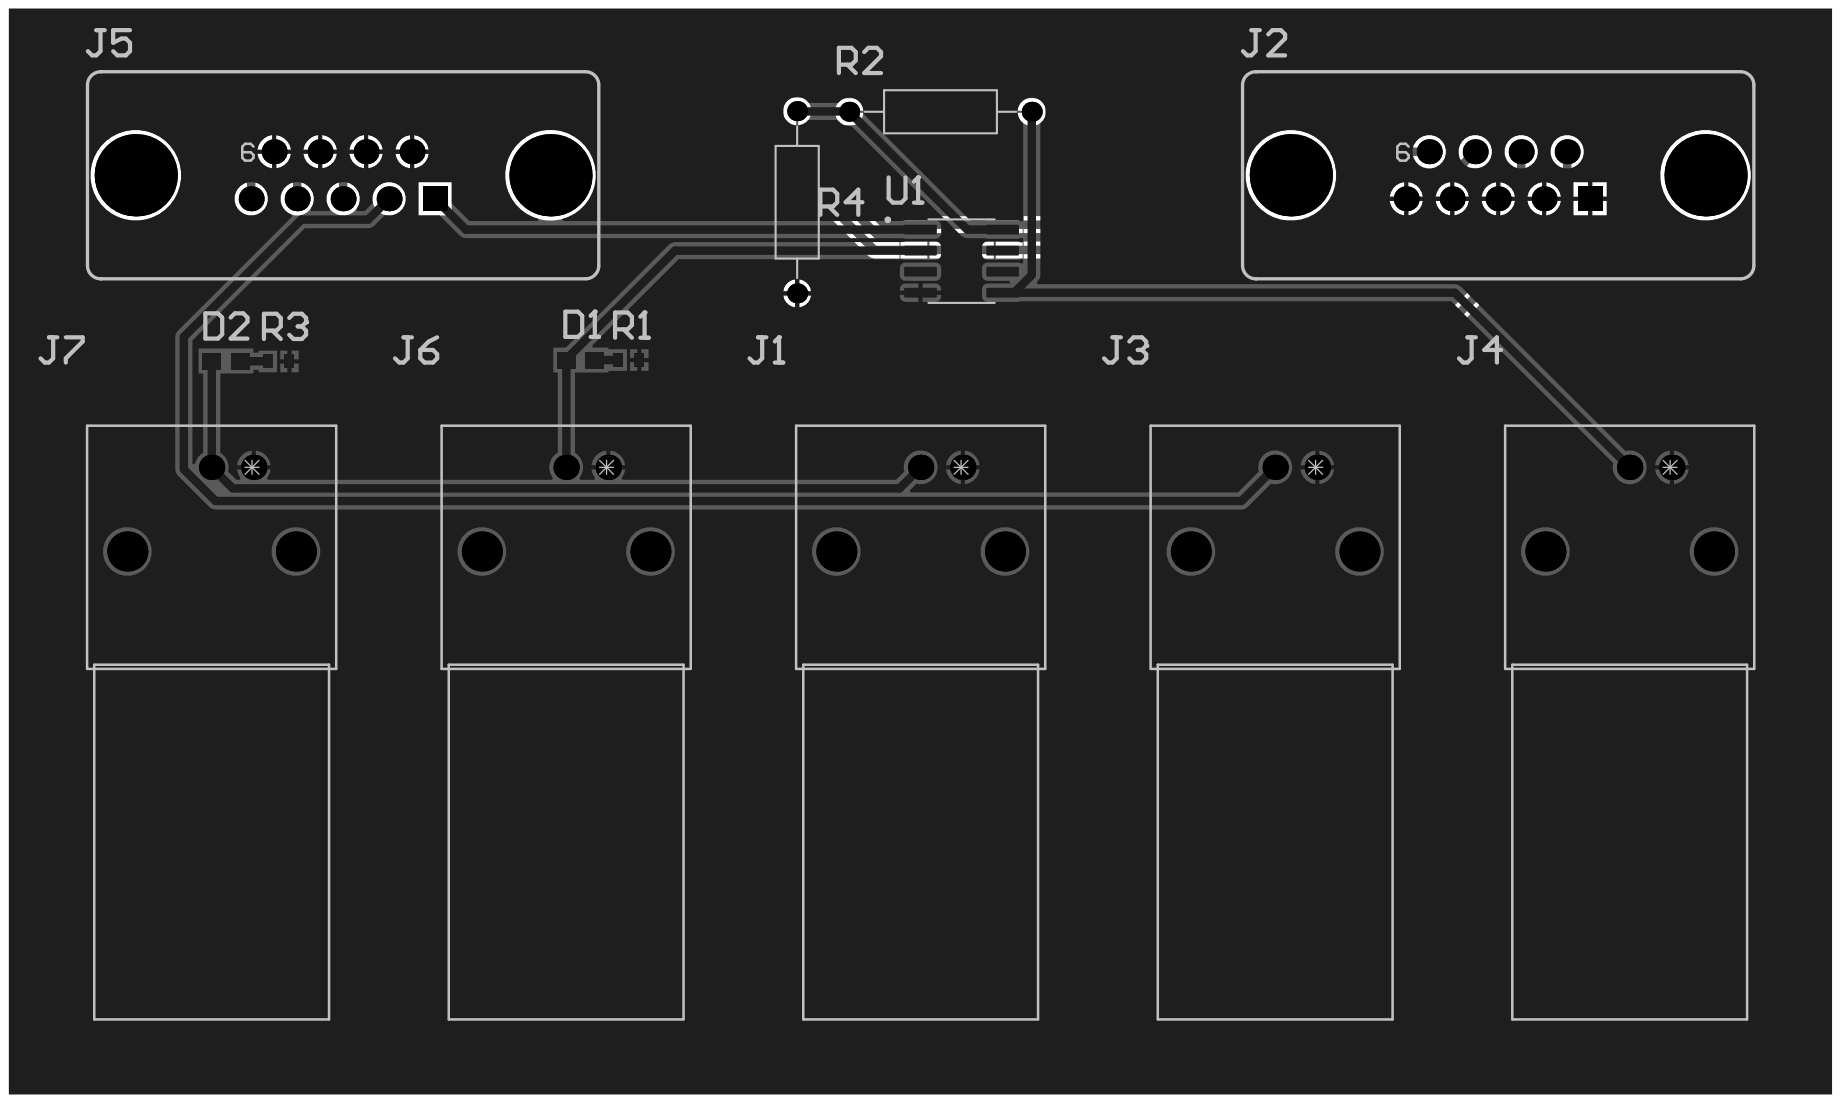
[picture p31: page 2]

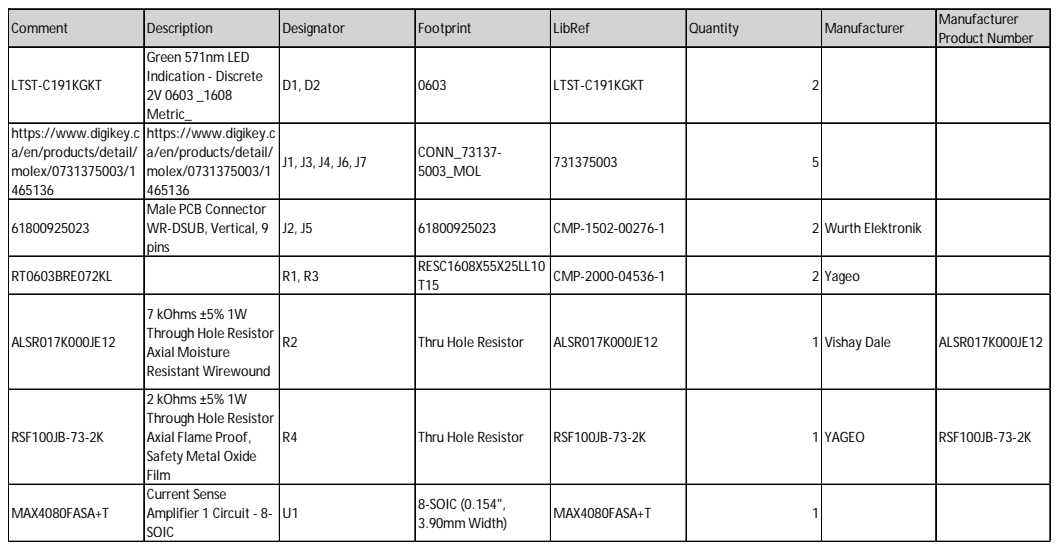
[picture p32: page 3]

Comment | Description | Designator | Footprint | LibRef | Quantity | Manufacturer | Manufacturer Product Number

LTST-C191KGKT | Green 571nm LED Indication - Discrete 2V 0603 _1608 Metric_ | D1, D2 | 0603 | LTST-C191KGKT | 2

https://www.digikey.ca/en/products/detail/molex/0731375003/1 465136 | https://www.digikey.ca/en/products/detail/molex/0731375003/1 465136 | J1, J3, J4, J6, J7 | CONN_73137-5003_MOL | 731375003 | 5

61800925023 | Male PCB Connector WR-DSUB, Vertical, 9 pins | J2, J5 | 61800925023 | CMP-1502-00276-1 | 2 | Wurth Elektronik

RT0603BRE072KL | | R1, R3 | RESC1608X55X25LL10 T15 | CMP-2000-04536-1 | 2 | Yageo

ALSR017K000JE12 | 7 kOhms ±5% 1W Through Hole Resistor Axial Moisture Resistant Wirewound | R2 | Thru Hole Resistor | ALSR017K000JE12 | 1 | Vishay Dale | ALSR017K000JE12

RSF100JB-73-2K | 2 kOhms ±5% 1W Through Hole Resistor Axial Flame Proof, Safety Metal Oxide Film | R4 | Thru Hole Resistor | RSF100JB-73-2K | 1 | YAGEO | RSF100JB-73-2K

MAX4080FASA+T | Current Sense Amplifier 1 Circuit - 8-SOIC | U1 | 8-SOIC (0.154", 3.90mm Width) | MAX4080FASA+T | 1

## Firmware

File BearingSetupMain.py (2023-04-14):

import csv
import nidaqmx
import pylab as plt
from nidaqmx import system
from threading import Thread

import settings
from Motor import motor_control
from Brake import brake_control
from CommandLineInterface import command_line_interface
from TorqueSensor import torque_sensor_control, torque_speed_sensor

# Channel Outputs: https://www.ni.com/docs/en-US/bundle/ni-daqmx/page/mxdevconsid/mydaqphyschanns.html

def main():
    settings.init()

    # Print out connected devices
    local = nidaqmx.system.System.local()
    for device in local.devices:
        print(f'Device Name: {device.name}, Product Type: {device.product_type}')
        print('Input channels:', [chan.name for chan in device.ai_physical_chans])
        print('Output channels:', [chan.name for chan in device.ao_physical_chans])

    # Use first device
    settings.program_running = True

    fig, ax = plt.subplots(nrows=2, ncols=2)
    plt.ion()

    ax[0, 0].set_title("Motor Voltage")
    ax[0, 0].axis(ymin=0, ymax=10)

    ax[0, 1].set_title("Motor Speed")

    ax[1, 0].set_title("Brake Voltage")
    ax[1, 0].axis(ymin=0, ymax=10)

    ax[1, 1].set_title("Brake Speed")

    torque_sensor_control_thread = Thread(target=torque_sensor_control, args=[local.devices[0].name])
    torque_sensor_control_thread.start()

    motor_control_thread = Thread(target=motor_control, args=[local.devices[0].name])
    motor_control_thread.start()

    brake_control_thread = Thread(target=brake_control, args=[local.devices[0].name])
    brake_control_thread.start()

    torque_speed_sensor_thread = Thread(target=torque_speed_sensor, args=[local.devices[0].name])
    torque_speed_sensor_thread.start()

    command_line_interface_thread = Thread(target=command_line_interface)
    command_line_interface_thread.start()

    while settings.program_running:
        # Control Voltage of the Motor
        motor_control_values_y_data = [i for i in settings.motor_control_values]
        motor_control_values_x_data = [i for i in range(len(motor_control_values_y_data))]
        ax[0, 0].axis(xmin=len(motor_control_values_x_data) - 1000 + 100, xmax=len(motor_control_values_x_data) + 100)
        ax[0, 0].plot(motor_control_values_x_data, motor_control_values_y_data, color="black")[0]

        # Speed of the Motor
        motor_speeds_y_data = [i for i in settings.motor_speeds]
        motor_speeds_x_data = [i for i in range(len(motor_speeds_y_data))]
        ax[0, 1].plot(motor_speeds_x_data, motor_speeds_y_data, color="black")

        # Control Voltage of the Brake
        brake_control_values_y_data = [i for i in settings.brake_control_values]
        brake_control_values_x_data = [i for i in range(len(brake_control_values_y_data))]
        ax[1, 0].axis(xmin=len(brake_control_values_x_data) - 1000 + 100, xmax=len(brake_control_values_x_data) + 100)
        ax[1, 0].plot(brake_control_values_x_data, brake_control_values_y_data, color="black")[0]

        # Speed of the Brake
        brake_speeds_y_data = [i for i in settings.brake_speeds]
        brake_speeds_x_data = [i for i in range(len(brake_speeds_y_data))]
        ax[1, 1].plot(brake_speeds_x_data, brake_speeds_y_data, color="black")

        plt.draw()
        plt.pause(0.01)

    with open("output.csv", 'w', newline='') as myfile:
        wr = csv.writer(myfile, quoting=csv.QUOTE_ALL)
        wr.writerow(settings.motor_control_values)
        wr.writerow(settings.motor_speeds)
        wr.writerow(settings.brake_control_values)
        wr.writerow(settings.brake_speeds)


if __name__ == '__main__':
    main()

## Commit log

2022-11-13 PCB Starting
    [Connectors.SchDoc, Control_Board.PcbLib, Control_Board.PrjPcb, Control_Board.SchLib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]
2022-12-08 What?! There's so many things! I hope no one reads these commits </3
    [Connectors.SchDoc, Control_Board.PcbDoc, Control_Board.PcbLib, Control_Board.PrjPcb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]
2022-12-17 End of V1
    [main.SchDoc]
2022-12-17 Board v2
    [BOM.xlsx, Control_Board.PcbDoc, Control_Board.PcbLib, Control_Board.PrjPcb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]
2022-12-27 Electrical works
    [output.csv]
